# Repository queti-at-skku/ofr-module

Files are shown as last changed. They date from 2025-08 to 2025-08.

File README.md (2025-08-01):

# 780nm Optical frequency reference Module Guideline 

In this project, we present a process of building a compact atomic optical frequency reference(AOFR) module with commerical, off-the shelf(COTS) optics. This device aims to provide precise and robust reference frequency source for wavelength meters, which is widely employed in optics laboratories. 

The entire system for laser frequency stabilization is integrated in 19" rack mountable case. 
In the module, the simple homemade optical block for saturated absorption spectroscopy(SAS) designed by web-based CAD, [Onshape](https://www.onshape.com/en/). The optical block designed using a beam-path-based methodology, in which each optical component is constrainted relative to the optical path to facilicate easy design modifications by user. 

Within the module, a Red Pitaya (STEMlab 125-14) perform PID locking and monitoring of the laser frequency.
By using user-friendly laser locking GUI [linien](https://github.com/linien-org/linien), user can easily control the entire system. 

All information of the design elements and COTS products is distributed via this page.

## Guideline 

### Overview 
The repository is organized into three parts:
- CAD files(.step, .stl) and drawings for custom subparts. 
- BOM list of COTS parts 
- DAG Metadata(.JSON file) of the SAS optics system. 

### Assemble and Installation 
---
1. Prepare the required subparts. Information of each components is available in the specified directory: 
    - COTS components 
        > .\AORF_module_BOM.xlsx
    - Base plate of optical block 
        > .\CAD drawings\SAS_plate\Machining_parts
    - Support base of optical components
        > .\CAD drawings\SAS_plate\3D_printed_parts
    - Enclousre 
        > .\CAD drawings\enclosure
2. Assemble the optical block, then connect the laser and verify that the spectroscopic signal.
    - Please refer to the following [Onshape link](https://cad.onshape.com/documents/0918872d287b7804801921a9/w/bc5e128b2e68215f23e08f09/e/3fa7893573c19a196d76a6ec) when assembling the block.
    - When verifing the signal with Redpitaya and linien, divide the photodiode output by using a bias tee before connecting to the device. For detail, refer to the [linien](https://github.com/linien-org/linien) documentation. 
    - If the spectroscopic signal exceed the measurement range, switch the jumper on the Redpitaya board to the HV. 
3. Once you have confirmed that the signal is present, configure the feedback loop using the Red Pitaya and Linien. In this case, the laser scan/mdoulation signal should be connected to the Koheron driver.
    - For the current modulation input on the Koheron driver, you can change the frequency range by adjusting the onboard jumper. For detail instructions, check the Koheron controller [User Guidline](https://www.koheron.com/support/user-guides/ctl200/).
4. If you configured the feedback loop in the previous step, the laser should be successfully locked. Integrate the system into the prepared enclosure, then verify once more that the spectroscopic signal is generated correctly. 
    - Please check the Onshape link and the "Optical Reference module" image below. 
5. If imporving lock quality of the module is required, Zeeman sublevel modulation can be employed instead of current modulation. See the "Zeeman sublevel modulation coil" section below. 

### Using the module 
---
At first run of the module, you need to setup a control PC. Install control GUI for each device:

| Device | GUI | connection | 
| ------ | --- | --- | 
| Laser controller | [CTL200 Graphical USer Interface](https://assets.koheron.com/gui/KoheronCTL200Setup0.4.0.exe) | Serial communication(USB) |  
| Redpitaya | [linien](https://github.com/linien-org/linien) | RJ45(LAN) | 

CTL200 also can be controlled directly by using serial communication. See [User Guidline](https://www.koheron.com/support/user-guides/ctl200/) of the device. Linien GUI and python client can be installed via PIP:

> pip install linien-gui

> pip install linien-client 

Overall status of the reference laser is controlled via CTL200 GUI. After turn on the laser, adjust the current setpoint to the specific laser power. Then, adjust the thermistor resistance setpoint to tune to the center frequency at the spectrosciopic signal appears. Ensure that the current scan via Redpitaya is enabled throughout this process. 

Further operation are performed by using linien. The tasks you can acrry out include the following:
- Frequency scan of the laser 
- Modulation signal configuration and frequeny Autolock. 
- Signal monitoring (Error, Feedback, Photodiode signal)
- Noise analysis (PSD)

See the [linien](https://github.com/linien-org/linien) page for instructions on setting up the GUI. 

## Remarks

### Optical Reference module scheme 



### Optical block 

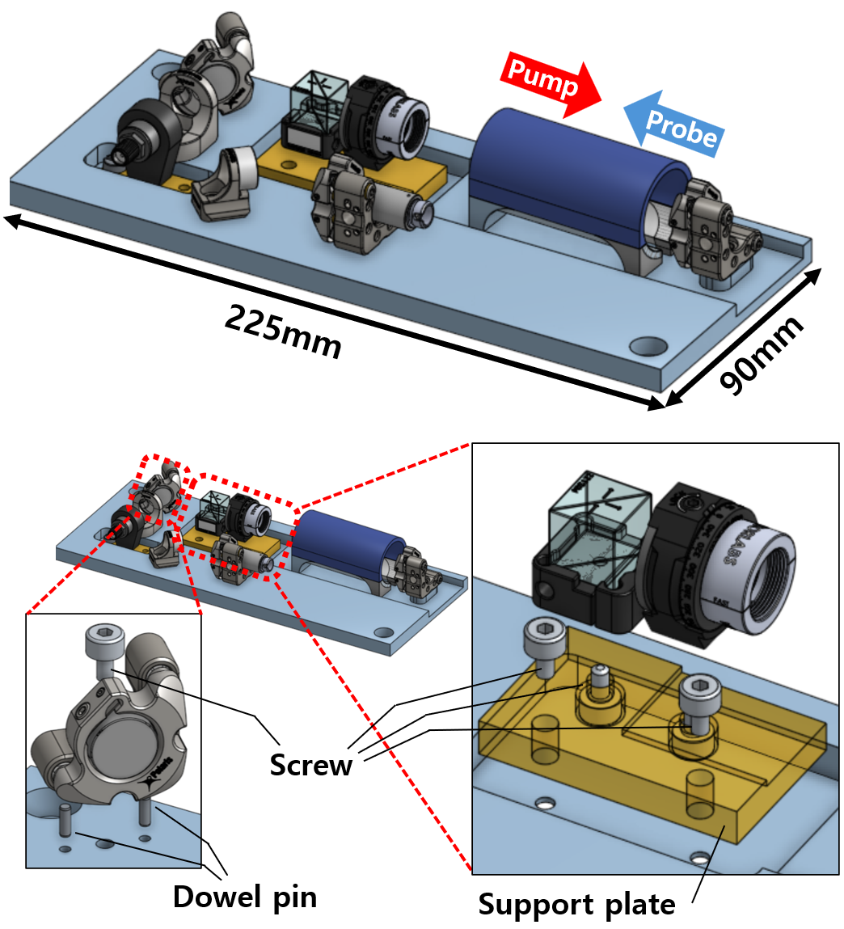
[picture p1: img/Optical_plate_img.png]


- The optical block is the SAS optical system arranged along an optimized beam path within a 225 mm × 90 mm footprint. Optical componets are mounted by using M4 screws and 2.1mm dowel pins. Some subparts require 3D-printed(or CNC machined) supports. 

### Zeeman sublevel modulation coil(ZMC coil)
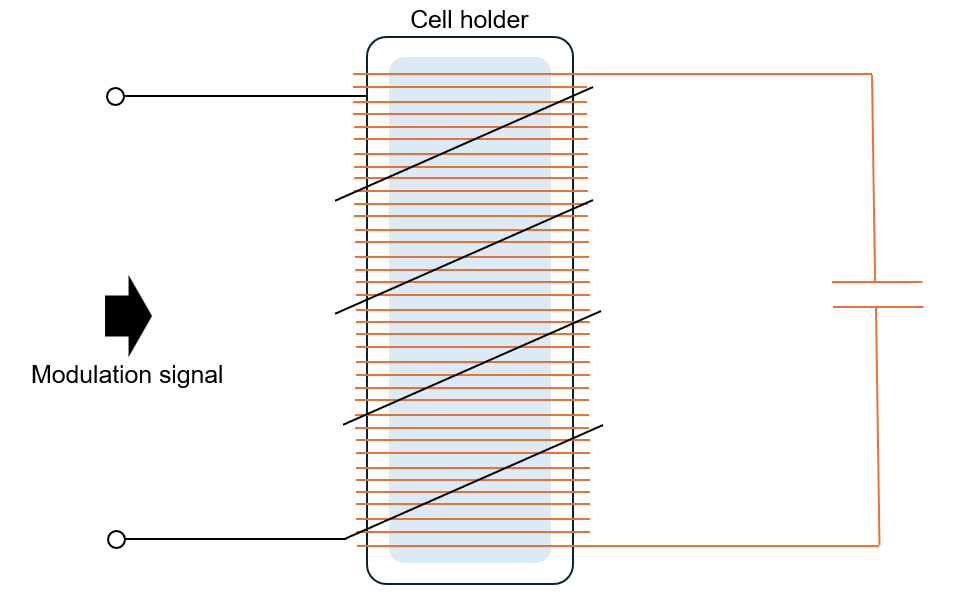
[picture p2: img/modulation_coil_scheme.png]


- To remove modulation frequency at the output laser frequency, modulation signal from the servo is applied to a solenoid which surrounded Rb cell and generate zeeman-sublevel modulation. 
- Rb atomic stretched state transition : **1.4MHz/Gauss**
- Wind enamel-coated wire around the cylindrical Rb cell holder to form a solenoid, then connect a capacitor across the solenoid's lead to config a LC circuit. 
    > Remark : Wind the coil with the Rb cell in place.
- Example of solenoid parameters:

    | Parameters | Values | 
    | ----- | --- | 
    | Wire thickness | 0.4mm |
    | Coil diameter | 28mm | 
    | Cell length | 50mm |
    | Number of turns | 120 | 
    | Capacitance | 100pF |
- You can sheiding magnetic field which generated at the solenoid by using mu-metal. 

## Reference 
[1] J. Wi, T. Kim, and J. Kim, "Compact and robust optical frequency reference module based on reproducible and redistributable optical design"
[2] B. Wiegand, B. Leykauf, R. Jördens, and M. Krutzik, “Linien: A versatile, user-friendly, open-source FPGA-based tool for frequency stabilization and spectroscopy parameter optimization,” Rev. Sci. Instruments 93, 063001 (2022).

## License 

## Disclaimer
The CAD representations of third-party components included in this material are the intellectual property of their respective owners and are provided here solely for reference and system integration purposes. We do not claim any copyright or ownership over these components. All rights remain with the respective rights holders.

## Acknowledgement  

This work was supported by the National Research Foundation of Korea (NRF) grant funded by the Korea government(MSIT) (2021R1F1A1062459,RS-2023-00302576,RS-2024-00466865
,2022M3H3A1063074) and Institute of Information \& Communications Technology Planning \& Evaluation (ITTP) grant funded by the Korean government(MSIT) (2022-0-01040).

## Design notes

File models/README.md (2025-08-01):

Instruction for CAD machining or printing

Table of recommended material, machining method (CNC or 3d printing or whatever)

Bolts & Nuts

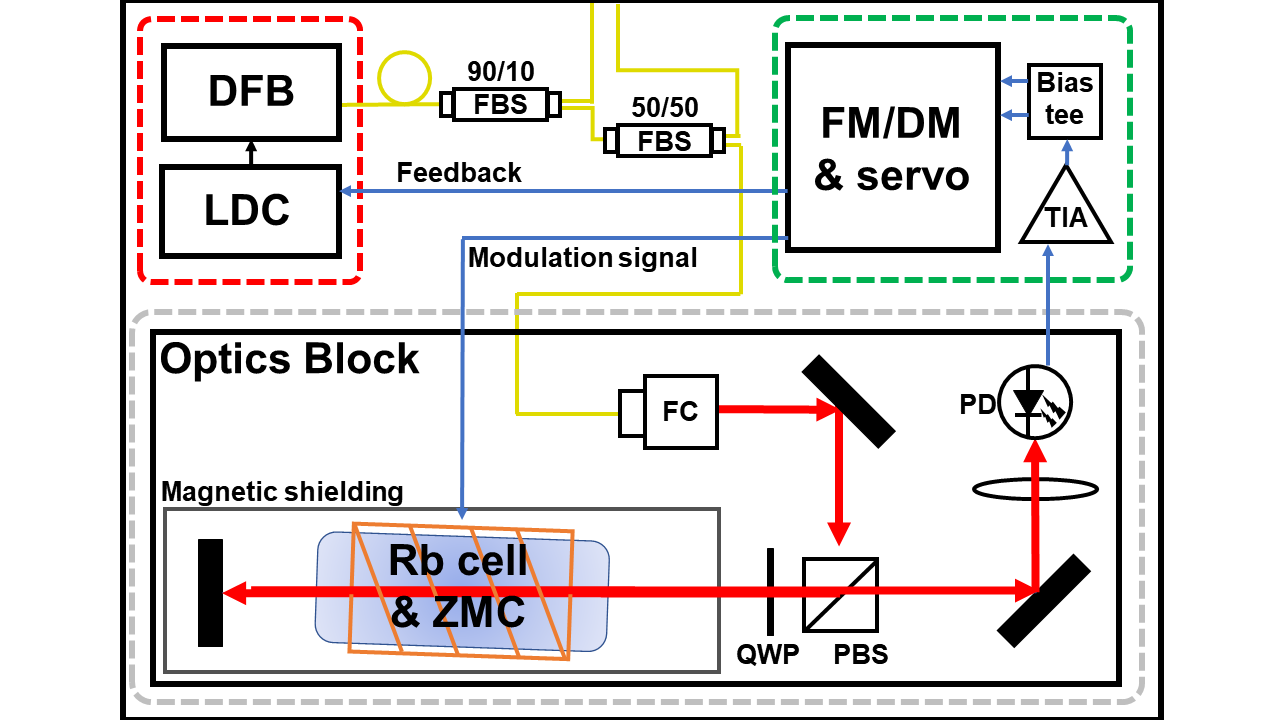
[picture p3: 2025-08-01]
img/electronical_connection.png

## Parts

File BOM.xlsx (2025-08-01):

No. | Item | Model Number | Qty
 | 780nm DFB Laser diode | Toptica EYP-DFB-0780-00010-1500-BFY12-0005 | 1
 | Laser controller | Koheron CTL200 | 1
 | RFSoC(Feedback Servo) | Redpitaya STEMlab 125-14 | 1
 | Rb cell |  | 1
 | 1/2" Polarizing Beamsplitter Cube, 620 - 1000 nm | Thorlabs PBS122 | 1
 | Platform Mount for 1/2" or 12.5 mm Beamsplitters and Right-Angle Prisms, M4 Tap | Thorlabs BSH05/M | 1
 | Ø1/2" Mounted Polymer Zero-Order Quarter-Wave Plate, SM05-Threaded Mount, 780 nm | Thorlabs WPQ05ME-780 | 1
 | Rotation Mount for Ø1/2" (Ø12.7 mm) Optics, M4 Tap | Thorlabs RSP05/M | 1
 | 780 nm, f = 18.40 mm, NA = 0.15 FC/APC Fiber Collimation | Thorlabs F280APC-780 | 1
 | Polaris® Ø1/2" Mirror Mount, 2 Low-Profile Hex Adjusters | Thorlabs POLARIS-K05S1 | 3
 | Polaris Ø1/2" Glue-In Fixed Mount, Optimized for Mirrors | Thorlabs POLARIS-C05G | 1
 | Mounted Silicon Photodiode, 320-1100 nm, Cathode Grounded | Thorlabs SM05PD3A | 1
 | Lens Mount with Retaining Ring for Ø1/2" Optics, M4 Tap | Thorlabs LMR05/M | 1
 | Ø1/2" Broadband Dielectric Mirror, 400 - 750 nm | Thorlabs BB05-E02 | 3
 | N-BK7 Plano-Convex Lens, Ø1/2", f = 15 mm, AR Coating: 400 - 1100 nm | Thorlabs LA1540-AB | 1
 | Polaris Ø1/2" Glue-In Fixed Mount, Optimized for Lenses | Thorlabs POLARIS-L05G | 1
 | Transimpedance Amplifier, 10 MHz Bandwidth, 10 kV/A Gain | Thorlabs AMP140 | 1
 | Passive Component Fiber Tray | Thorlabs BFCT | 1
 | 1x2 PM Coupler, 780 ± 15 nm, 50:50 Split | Thorlabs PN780R5A1 | 1
 | FC/PC to FC/PC or FC/APC to FC/APC Mating Sleeve | Thorlabs ADAFCPM2 | 1
 | FC/APC to FC/APC Dual L-Bracket Mating Sleeve | Thorlabs ADAFCB4 | 1
 | Optical plate |  | 1
 | 1U 19" rack case |  | 1
 | 5V10A SMPS | LM50-20xx | 1
 | USB port |  | 1
 | Power plug |  | 1
 | LAN port |  | 1

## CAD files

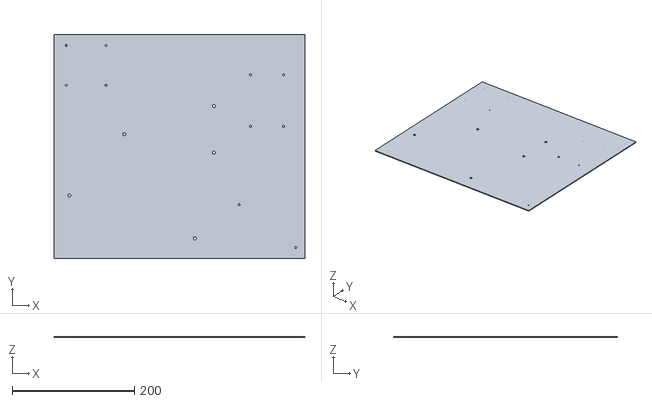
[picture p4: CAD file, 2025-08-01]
models/enclosure/module_rack_base.stl
410.0 x 366.0 x 1.50

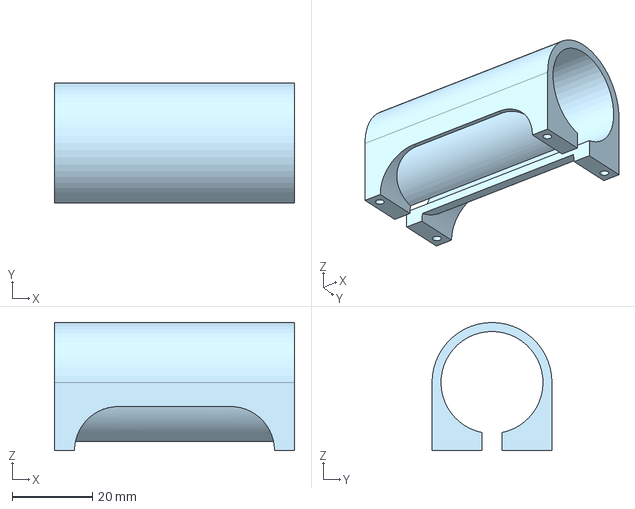
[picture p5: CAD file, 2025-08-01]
models/SAS_plate/3D_printed_parts/Rb_Cell_holder_CAD.step
60.0 x 30.0 x 32.0 mm

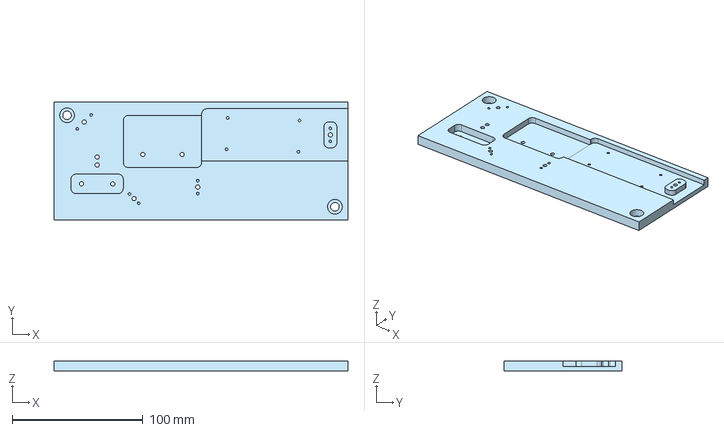
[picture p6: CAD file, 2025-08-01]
models/SAS_plate/Machining_parts/Base_plate_CAD.step
225.0 x 90.0 x 8.00 mm

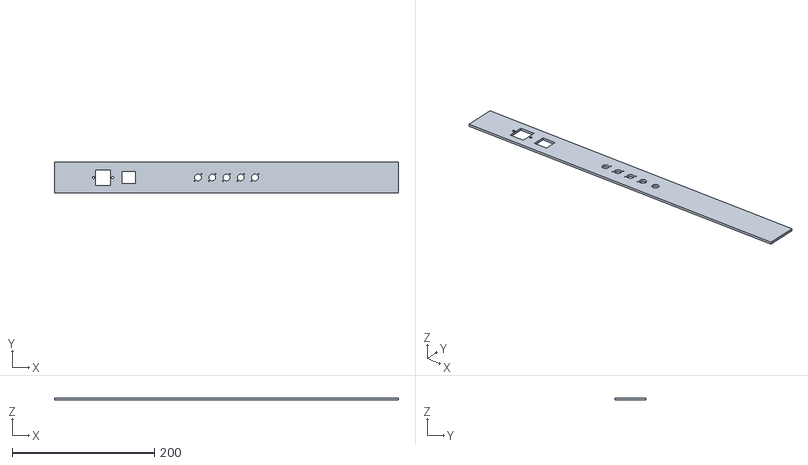
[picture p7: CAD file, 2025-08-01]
models/enclosure/module_rack_front.stl
483.0 x 43.0 x 3.00

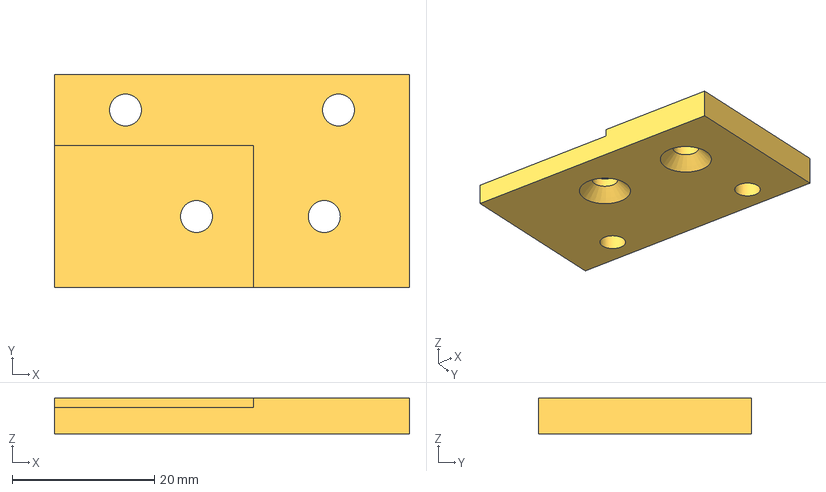
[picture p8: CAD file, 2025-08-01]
models/SAS_plate/3D_printed_parts/PBS_waveplate_base_CAD.step
50.0 x 30.0 x 5.00 mm

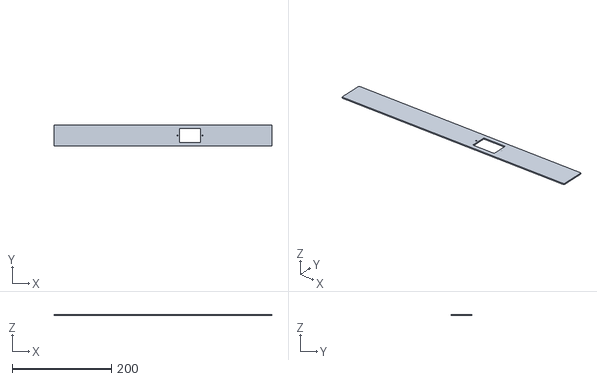
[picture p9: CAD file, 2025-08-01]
models/enclosure/module_rack_back.stl
440.0 x 43.0 x 2.00

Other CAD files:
models/SAS_plate/Machining_parts/Drawing/base_plate_drawing.dwg
